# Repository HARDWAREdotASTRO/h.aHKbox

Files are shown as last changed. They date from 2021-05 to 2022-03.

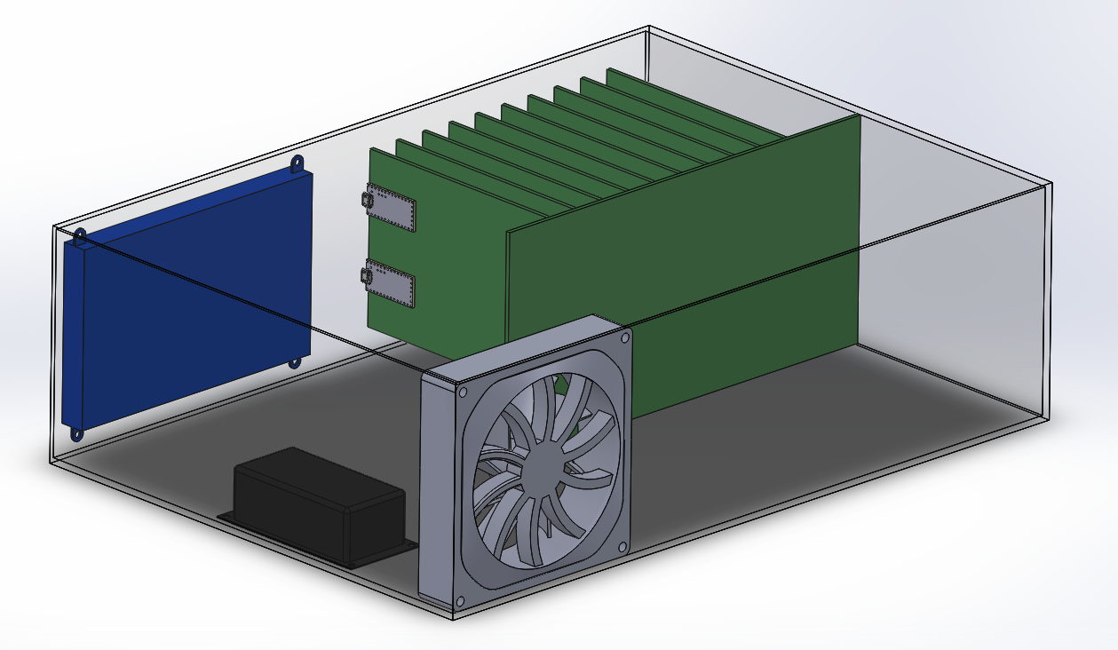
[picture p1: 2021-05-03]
Chassis/3d/Assembly - FULL/Pics/AssemblyCaptureBack0.1.PNG

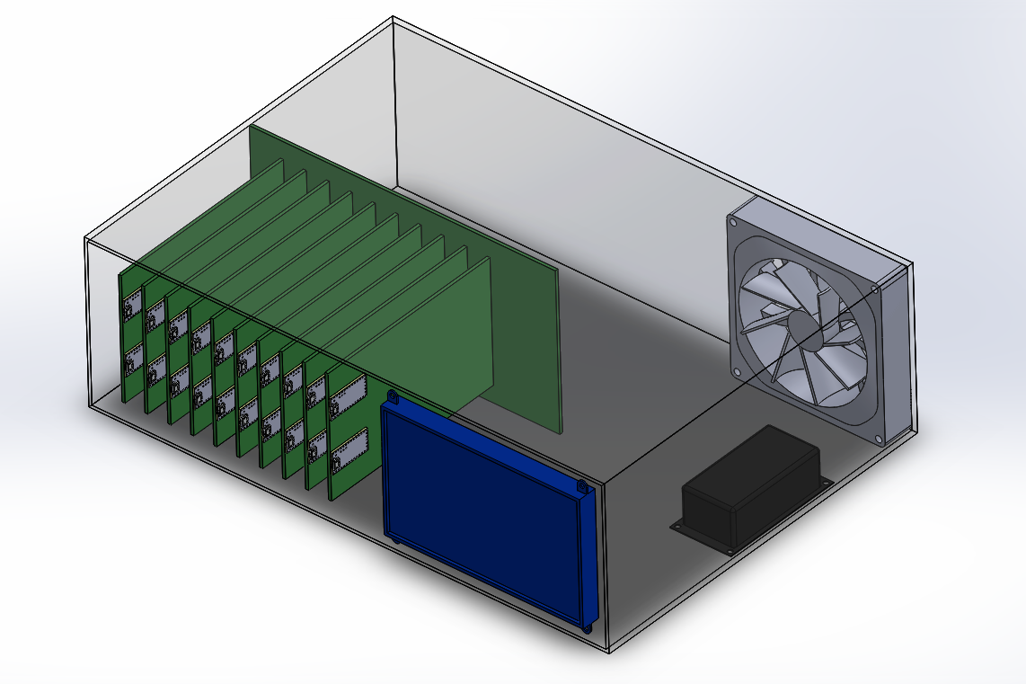
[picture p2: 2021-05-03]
Chassis/3d/Assembly - FULL/Pics/AssemblyCapture0.1.PNG

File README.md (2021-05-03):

This project was presented in progress at the 235th AAS confernece in Honolulu, HI in January of 2020. The submitted abstract for this presentation can be found here: https://ui.adsabs.harvard.edu/abs/2020AAS...23517507S/abstract

# H.aHkBox
The Hardware.astronomy Housekeeping Box (H.aHkBox) is an open source modular platform originally designed for the monitoring and control of temperatures on the ZEUS2 grating spectrometer. I began working on this project under the direction of Dr. Carl Ferkinhoff in May of 2019 and continue to do so (Dec 2020). 

Additional information about ZEUS2 can be found here: http://hosting.astro.cornell.edu/~spifiweb/zeus2/index.html

Additional information about the H.aHkBox will be made available on OSF in the future.

## Motivations
Existing temperature control equipment for the ZEUS2 is limited for various reasons. Chief among them are:
  - Obsolete components that cannot be replaced if/when they break
  - Temperature reading rate is limited by hardware multiplexer
  - System is dependent on external PC
  
The H.aHkBox is an attempt to solve these issues while providing a versatile platform for future growth of ZEUS2 and other projects.

## Specific Goals
  - [X] Design and build the chassis 
  - [X] Design and build a prototyping modular card
  - [ ] Design and build the backplane of the system [in progress]
  - [ ] Design and program an operating system (H.aHkOS) and supporting libraries [in progress]
  - [ ] Design and build ZEUS2 specific modular cards [in progress]

See h.aHKbox\Chassis\Presentation\Presentation\December 2020\ for a presentation detailing the process and current state of the project.

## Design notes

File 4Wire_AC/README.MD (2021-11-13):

<h1>4 Wire AC Expansion Card</h1>

Documentation of all firmware (in C++ for Teensy) and circuit designs for WAG implemented solution to a 4 wire AC expansion card under the H.aHK Box Project.
<br><br>

<h3>Project Background:</h3>

A 4 wire AC temperature measurement circuit is proposed for interface between the H.aHK Box (Hardware.astronomy Housekeeping Box) and the Zeus-2 Spectrometer <sup>a</sup>. Specifically, the Zeus-2 Spectrometer temperature region of interest in application of this circuit operates down to about 100 mK. The Zeus-2 spectrometer uses Lake Shore Cryogenics Interchangeable ROX sensors mainly, but also uses some Germanium GR300 sensors as well <sup>b</sup>.
<br><br>
<h3>Design Specifications</h3>
- System reports temperature value at up to 10 sps <br>
- Obtain resolution of &#177; 10mk in sub-milliKelvin scale and &#177; 1K at higher temperature ranges <br>
- Optimize (minimize) power dissipation across sensor to minimize heat dissipation into low temerature region <br>
- Optimize circuit for low component count <br>
- Digitize read in and output to circuit (frequency output, etc.) <br>
- Optically isolated sensor from digital circuitry <br>
- Operature through +5V and +24V lines <br>
- Interface with H.aHK Box systems and software/firmware communication protocols <br>
<br><br>

<h3>Project Staff</h3>
- Stephen Shaw (General Engineering, Electronics), May 2020 - May 2022

<br><br>
<h3>References</h3>
<sup>a</sup> - https://www.researchgate.net/publication/47351146_ZEUS-2_A_second_generation_submillimeter_grating_spectrometer_for_exploring_distant_galaxies
<br>
<sup>b</sup> - https://www.lakeshore.com/products/categories/temperature-products/cryogenic-temperature-sensors

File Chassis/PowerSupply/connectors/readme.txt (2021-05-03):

Power connector information in this folder

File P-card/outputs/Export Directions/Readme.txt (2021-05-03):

I had a lot of trouble with exporting from CircuitMaker, but eventually I figured it out!

I strongly recommend you use the "Outputs" tab while editing a circuitboard file, rather than "Project -> Generate Outputs" as the latter option generates all outputs for every board in the project which can get confusing.

Issues I ran into:
1. "Board Cutout" and "Board Shape" have nothing to do with the actual board shape. They are just there so you know where you can put your components. To tell the manufacturer the shape of the board you need to use lines to draw the board outline on the "Keep-out Layer" Layer. 
	-> If there is no pre-existing keepout layer, you can open the "View Configurations" Layer window by clicking on the small colored rectangle to the left of the layer tabs at the bottom of the circuit board window. This should list all of the layers and their colors. From here you want to look at the Mechanical Layers(M) table on the top right. Uncheck the "Only show enabled mechanical Layers" box if it is checked. Enable one of the unused Mechanical Layers using the "Enable" check box. Slowly click twice on the name of the layer so you're able to edit the name. Rename it to "Outline". Check the "Show" box for this layer, and then click "OK" at the bottom right of the window. Now you should have the "Outline" Layer listed in the tabs at the bottom, and you can draw your board outline.

2. Wonky Top Overlay drawings resulted in the Gerber Viewer when I uploaded the files wihtout any explanation. I had followed the same process that worked not 20 minutes prior to export my files, so I had no idea what caused it. After a lot of creative googling I found one forumn post where someone suggested use "Relative Origin" instead of "Absolute Origin" in the file output configurations. This did indeed fix my issue, but you NEED to make sure you use relative origin for both the gerber output and the nc drill output. If they arn't the same, the holes may end up offset!

OUTPUT STEPS:
1. Save your files and commit them.
2. With your board file open, goto the "Outputs" tab and click the "Gerber" button.
		- if you are prompted to save, click yes, click ok
3. In the pop up you can change your setting as needed. The mains ones I messed with:
		General -> Units = millimeters
		General -> Format = 4:3
		Layers -> All Layers -> Plot = checked (everything else unchecked
					-----> if you used a mechanical layer instead of the "Keep-out layer", make sure its "Plot" checkbox is checked in the right side of this layer tab. Otherwise it won't be part of the outputs.
		Drill Drawings -> Plot all used layer pairs = both boxes checked
		Apertures -> Embedded apertures (RS274X) = checked
		Advanced -> Position on File = Reference to relative origin
		Everything else left default
4. Click OK and save to desired location

5. In the Outputs tab, click "NC Drill Files" and save/commit if prompted.
6. Settings I chose are as follows
		Units = Millimeters (same as gerber)
		Format = 4:3 (same as gerber)
		Coordinate Positions = Reference to relative origin (same as gerber)
		Everything else left default
7. Click OK and save to desired location (preferably near gerber output)
8. Next, the gerber and NC Drill files need to be combined into one zip file. 
	- Using your desired program, Extract the contents of both the gerber output and the nc drill output.
	- Create a new zip file and add both outputs to it.
		- You will be prompted to overwrite the StatusReport.txt, to which you can say yes.
9. The resulting zip is the file you will need to upload to the manufacturer.
10. I suggest you use an online Gerber Viewer to make sure the files load in the way you expect them to. 
		https://www.pcbway.com/project/OnlineGerberViewer.html   is what I used as we were ording from PCBWay anyway. If you're ordering from a different manufacturer and they have a their own viewer, I suggest you use theirs as it will likely be more accurate to their process.

If you have any questions you can contact me at adam.stammer@go.winona.edu or adam.r.stammer@gmail.com

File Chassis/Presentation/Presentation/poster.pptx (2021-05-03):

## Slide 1

HARDWARE.astronomy: Housekeeping Box (H.aHkBox)

Here we present the HARDWARE.astronomy Housekeeping Box (H.aHkBox). The H.aHkBox is a low-cost open-source temperature monitoring and control system. It employs existing open-source devices (e.g Arduino, RaspberryPi) to reduce costs while also limiting the complexity of the development. The H.aHkBox features a chassis with a variety of capabilities, a control computer, and 10 expansion slots that can be populated by expansion cards. The first deployment of the H.aHkBox will be for the ZEUS-2 submillimeter grating spectrometer. As such the modular cards will include AC and DC excited 4-wire bridges, 2-wire bridge, and PID controller card. The system can output up to 200W, and achieve sub-millikelvin temperature sensing accuracy. Design, firmware, software and parts list will be published online allowing for other projects to adopt the system and create custom expansion cards as needed. Here we provide an overview of the project, initial layout of the chassis, electrical design, and specifications, as well as a proto-type expansion card.

Abstract

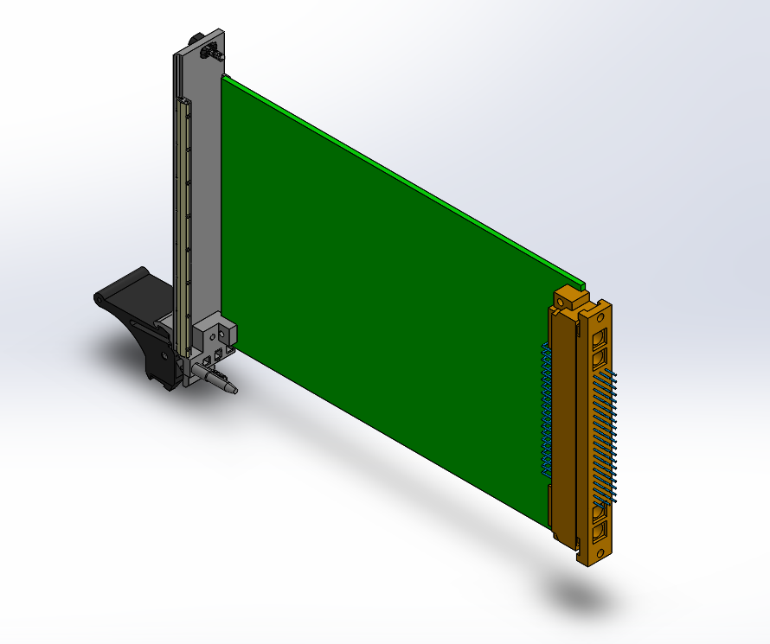
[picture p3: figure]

Background/Requirements

Prototyping Card

Backplane

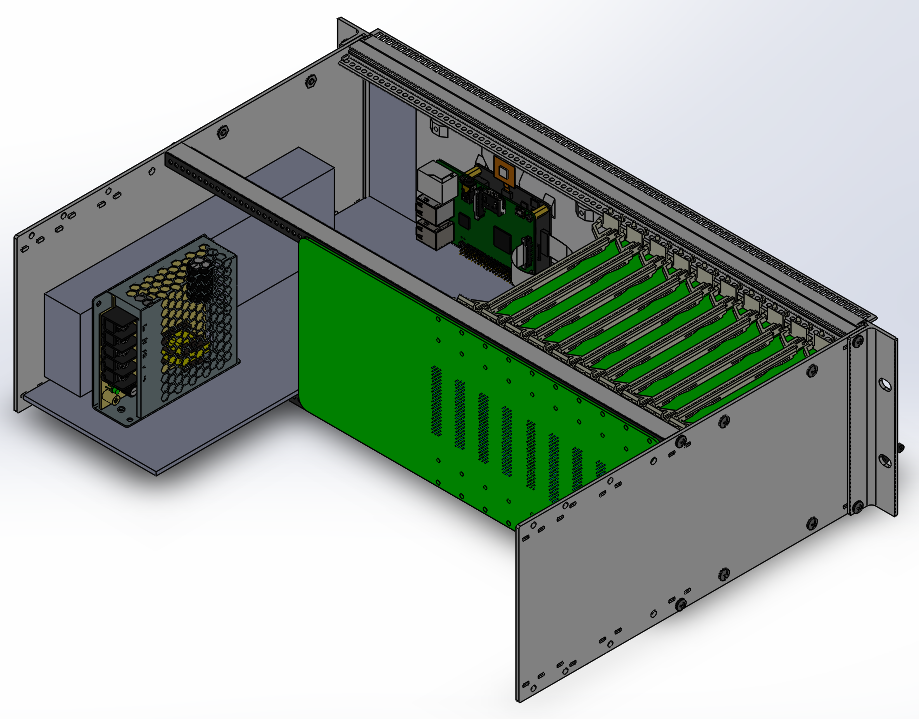
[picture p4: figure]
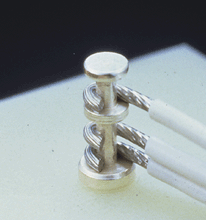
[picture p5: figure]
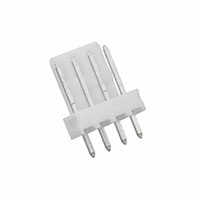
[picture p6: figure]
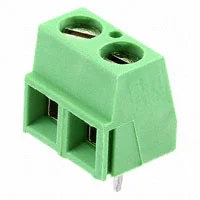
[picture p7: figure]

Interface

Physical Design and Interface

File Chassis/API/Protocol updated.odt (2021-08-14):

Logistical Header | Source Card Type | [Data Frame 1] | [Data Frame 2] | [Data …] | [Data Frame n]

0 4 8 16 24 32 n

Logistical Header:

Logistical Request → (0x0) Used to poll Followers for information.

Logistical Response → (0x1) Responds to Logistical Request. Followed by yes/no data frame.

Error → (0x2) Used to report an error.

Data → (0x3) Used to send non-logistical data.

Acknowledgement (0x4) Sent to follower devices to say message was received

Boot (0x5) When booting up sends information to slave

Interrupt (0x6) Allows for slaves to interrupt connection

Command Request (0x7) request to send a command to Follower device

Command Response (0x8) Responds to receive message of command (acknowledges before performing the command

Logistical Request Format

0b0000 | Source Card Type

0 4 8

This is sent to a slave to ask if there is any message for the master to read from it. The slave will always respond with a logistical response. If the Logistical Request times out, it will be viewed as an error. In such a timeout case, the slave may be assumed non-responsive or not installed into the motherboard and may be taken out of the communication update loop.

Logistical Response Format

0b0001 | Source Card Type | (0b0 / 0b1) , Buffer Size

0 4 8 9 16

This is sent back to the master in response to a Logistical Request. It contains only the Logistical Header and one 8-bit data frame. The first bit in the data frame answers a yes or no to the question. 0 indicates that there is data to read from the slave, while a 1 indicates that there is not. The remaining 7 bits in this data frame denote the amount of sequential bits of data to be read. Since I2C reads 8-bit data frames, rather than direct bits, it is suggested that any data is built in 8 bit blocks, though extra bits can simply be ignored.

Error

0b0010 | Source Card Type | Error Type

0 4 8 16

The Error Header is used to report an error to the master. Error Type is an 8-bit data frame that denotes the error code. These error codes will be card specific, so they can only be defined as part of the card design. Since there are 16 reportable card types and one 8-bit data frame for the error code, it’s suggested that error codes are defined by card type as denoted below, though this isn’t required.

Card Type | Error Code Range | Card Type | Error Code Range
0 | 0-4095 | 8 | 32768-36863
1 | 4096-8191 | 9 | 36864-40959
2 | 8192-12287 | A | 40960-45055
3 | 12288-16383 | B | 45056-49151
4 | 16384-20479 | C | 49152-53247
5 | 20480-24575 | D | 53248-57343
6 | 24576-28671 | E | 57344-61439
7 | 28672-32767 | F | 61440-65535

Data

4-wire AC (Card Type 0x2)

Input

0b0011 | 4 wire AC (card) | Specific Card Data ---- >

0 4 8 48

4 - Wire AC (Card Data)

Channel number | On/Off | Voltage flag | Range | 32-bit Resistance data
0b000 | 0b0 | 0b0 | 0b000 | 0b0000 0000 0000 0000…. 0000
0b001
0b010
0b011

8 11 12 13 16 48

Channel number:

4 channels each on will contain a setting for whether the channel will be on or off and what the range that channel will be.

On/Off:

1 value for on

0 Value for off

Voltage flag:

Using the extra byte from the range to be a voltage flag. When 1 it means the number is returning a voltage when low it is returning a resistance value

Range:

| Range

0 4

Represent the possible range of resistance that can be used by the 4 wire ac. This uses only three bits originally it was 4 with a buffer zero value but the extra zero bit is now going to be used a Boolean to represent if the data being received is a voltage or a resistance.

Flag | 000 | 10K Ω
| 001 | 100KΩ
| 010 | 1MΩ
| 011 | 10MΩ

0 1 4

16 bit Resistance Data

If we are using decimal numbers in returning back resistance values then the

*Changed to 32 bits precision of byte data*

This is intended to be a scientific notation of data

8 bits to represent the whole number with 24 bits of decimal point precision using mantissa binary numbers

Some bits will be reserved to represent as an exponential value.

Currently we can used the last 8 bits of the 24 decimal point precision as exponential (max value of 255) or signed bit ( 127 to -128)

Higher resistance is needed for when it gets below 1 K due to self heating

Difference modes when different resistors are attached to the 4 wire ac card

The card will have to convert the voltage or resistance into scientific notation. The scientific notation of the conversion will be displayed onto the GUI.

4 Channels

Measuring 4 temperatures (change in resistance) uses 16 bits of double precision

Returns a resistance that ranges from ~100ohm to 100Kohm

Error:

Time out

Could not detect master – time out

Could not understand master request

Value in sent to device does not make sense

Boot

0b0100 | Source card

0 4 8

The initial message the master sends out for slaves to respond to. The slaves are to respond with their typical logistical response with what card they are but they will have no data attached to them, so they will send all zeros. On this initial boot the Master will wait for a response from each possible card and then add each card to the round Robin while loop if the corresponding source card responds within a certain time limit. There is a possible of 10 max cards so the increment of the source card number will max at 10 (Actually at 0b0111)

Interrupt

0b0101 | Source Card Type | Interrupt data

0 4 8 16

Triggers an interrupt to happen to allow the card to break the master out of the Round Robin. It has the interrupt trigger and what source card and telling the master what it wants to do. The master will handle the Interrupt before going back to what it was doing. Once the interrupt is finished the master will continue its while loop rounds of all the cards registered as slaves, checking for information.

Command Request

0b0111 | Source card type | Command type list

This will be used by the Leader device to send to Follower to have them perform a command

Possible commands to be used (functions vary from card to card):

Shutdown

Change settings

Temp

Voltage or resistance data

Resistance range

Command Response

0b1000 | Source card type | Data?

0 4 8

An acknowledgement that the card has received the command.

(card will acknowledge After doing command)

Not sure if a data portion is going to be needed could be used as something similar to logistical requestion to write if the card has any new data to report after the command has been executed. (NOTE: if data portion is not needed then the acknowledgement can be send before performing the command. This data can also instead be sent as either a regular round robin or a interrupt instead)

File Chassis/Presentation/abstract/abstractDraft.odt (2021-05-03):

Abstract (H.aHKbox)

Here we present the HARDWARE.astronomy Housekeeping Box (H.aHKbox. The H.aHKbox is a low-cost open-source temperature monitoring and control system, which employs existing open-source devices (e.g Arduino, RaspberryPi) to reduce costs while also limiting the complexity of the development. The Ha.HK Box features a base system with a control computer and 10 expansion slots that can be filled with a variety of expansion cards.

The first deployment of the Ha.Hkbox will be for the ZEUS-2 submillimeter grating spectrometer. As such the modular cards will include AC and DC excited 4-wire bridges, 2-wire bridge, and PID controller card. The system will achieve power outputs of up to 200W with sub-millikelvin temperature sensing accuracy.

All design, firmware, software and parts list will be published online allowing for other projects to adopt the system and create custom expansion cards as needed.

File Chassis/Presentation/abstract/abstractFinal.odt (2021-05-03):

HARDWARE.astronomy: Housekeeping Box (H.aHk Box)

Here we present the HARDWARE.astronomy Housekeeping Box (H.aHk Box). The H.aHk Box is a low-cost open-source temperature monitoring and control system. It employs existing open-source devices (e.g Arduino, RaspberryPi) to reduce costs while also limiting the complexity of the development. The H.aHk Box features a chassis with a control computer, and 10 expansion card slots that can achieve a variety of capabilities. The first deployment of the H.aHk Box will be for the ZEUS-2 submillimeter grating spectrometer. As such the modular cards will include AC and DC excited 4-wire bridges, 2-wire bridge, and PID controller card. The system can output up to 200 watts, and achieve sub-millikelvin temperature sensing accuracy. The schematics, firmware, software and parts list will be published online allowing for other projects to adopt the system and create custom expansion cards as needed. Here we provide an overview of the project, initial layout of the chassis, electrical design, and specifications, as well as a proto-type expansion card.

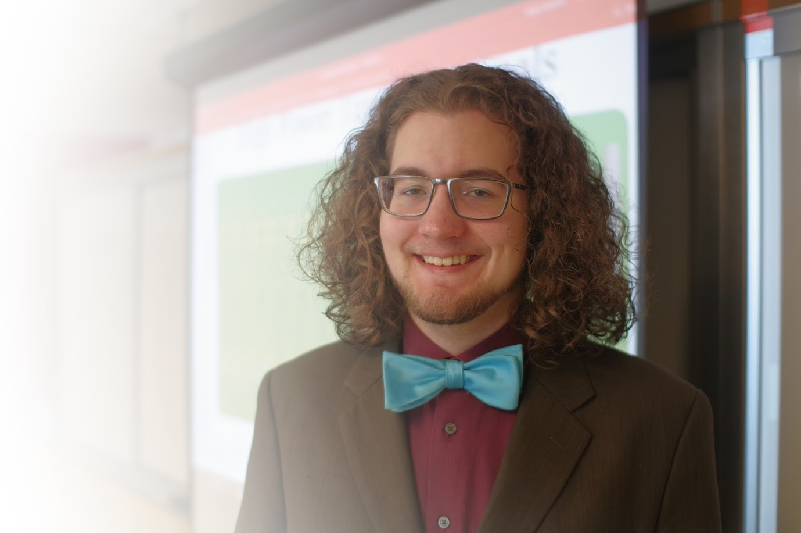
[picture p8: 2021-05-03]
Chassis/Presentation/Presentation/figures/posterPhoto.png

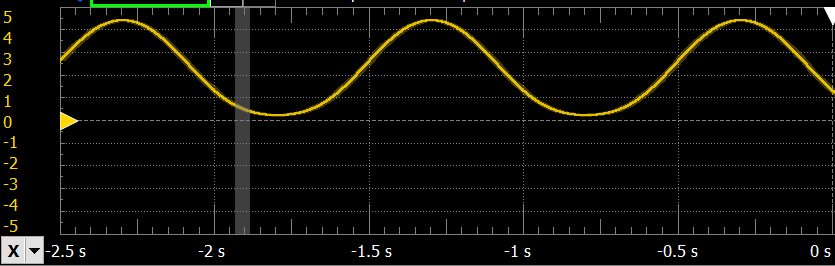
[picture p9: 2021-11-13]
4Wire_AC/LabFiles/LAB004_DesignViabilityAnalysis/Part1_Trace_Vmod1.PNG

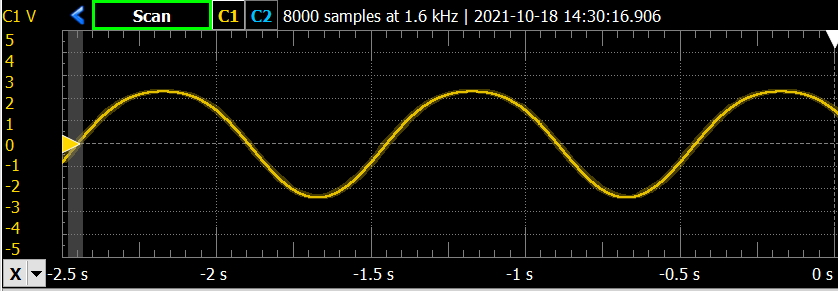
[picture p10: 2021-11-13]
4Wire_AC/LabFiles/LAB004_DesignViabilityAnalysis/Part1_Trace_InstAmp.PNG

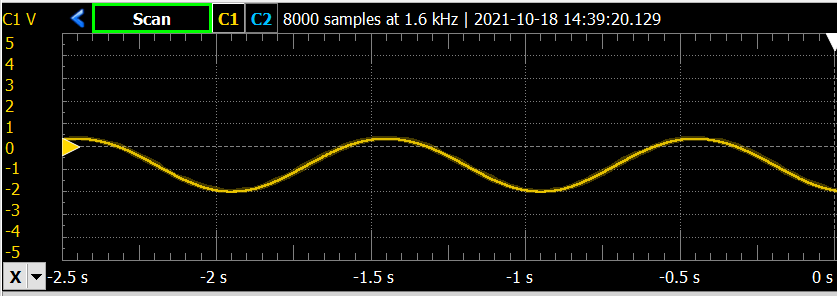
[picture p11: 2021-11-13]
4Wire_AC/LabFiles/LAB004_DesignViabilityAnalysis/Part1_Trace_InstAmp2.PNG

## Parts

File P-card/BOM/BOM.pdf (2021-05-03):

Sheet1

All Prices Are Subject to Change | Compiled July of 2019 by Adam Stammer
All Prices Based On Single Unit Price

P-Card BOM
Part Name/Description | Supplier Part # | Supplier | Manufacturer Mfct. Part # Unit Cost | Quantity | Total Cost
P-Card PCB | Varies | 1 Varies
Female Socket | 1195-4236-ND | Digikey | Harting | 9032606865 | 9.48 | 1 | 9.48
Male Socket | 1195-1147-ND | Digikey | Harting | 9031606901 | 10.67 | 1 | 10.67
Banana Jack | BKCT3151SP-0-ND | Digikey | Cal Test Electr CT3151SP-0 | 2.05 | 4 | 8.2
Breadboard (10”x3.5” max) | BKGS-830-ND | Digikey | Global Special | GS-830 | 8.25 | 1 | 8.25
Teensy 3.x | 1528-2385-ND | Digikey | Adafruit Indust | 2756 | 24.94 | 1 | 24.94
RA Din-Signal Hi Current Pin | 1195-1112-ND | Digikey | Harting | 9030006104 | 7.22 | 2 | 14.44
Total (USD) | 75.98

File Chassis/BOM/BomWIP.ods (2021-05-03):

All Prices Are Subject to Change | Compiled July of 2019 by Adam Stammer
All Prices Based On Single Unit Price
P-Card BOM
Part Name/Description | Supplier Part # | Supplier | Manufacturer | Mfct. Part # | Unit Cost | Quantity | Total Cost
P-Card PCB |  |  |  |  | Varies | 1 | Varies
Female Socket | 1195-4236-ND | Digikey | Harting | 9032606865 | 9.48 | 1 | 9.48
Male Socket | 1195-1147-ND | Digikey | Harting | 9031606901 | 10.67 | 1 | 10.67
Banana Jack | BKCT3151SP-0-ND | Digikey | Cal Test Electronics | CT3151SP-0 | 2.05 | 4 | 8.2
Breadboard (10”x3.5” max) | BKGS-830-ND | Digikey | Global Specialties | GS-830 | 8.25 | 1 | 8.25
Teensy 3.x | 1528-2385-ND | Digikey | Adafruit Industries | 2756 | 24.94 | 1 | 24.94
RA Din-Signal Hi Current Pin | 1195-1112-ND | Digikey | Harting | 9030006104 | 7.22 | 2 | 14.44
 |  |  |  |  |  | Total (USD) | 75.98
Backplane BOM
Part Name/Description | Supplier Part # | Supplier | Manufacturer | Mfct. Part # | Unit Cost | Quantity | Total Cost
Backplane PCB |  |  |  |  | Varies | 1 | Varies
Female Socket | 1195-4236-ND | Digikey | Harting | 9032606865 | 9.48 | 10 | 94.8
4 Pin Socket | WM50016-04-ND | Digikey | Molex | 22284043 | 0.4 | 90 | 36
2 Pos Screw Terminal | 283-4439-ND | Digikey | Eaton – Electctronics Div. | EM250502V | 1.01 | 12 | 12.12
Turret Terminal | 952-1453-ND | Digikey | Harwin Inc. | H9021-01 | 0.43 | 33 | 14.19
 | Z9021-00-ND | Digikey | Harwin Inc. | Z9021-00 | 343.68 | 1 | 343.68
Arduino Uno Rev 3 | Rev 3 | Arduino Store | Arduino | Rev 3 | 22 | 1 | 22
Arduino Heads | 1528-1074-ND | Digikey | Adafruit Industries | 85 | 1.95 | 1 | 1.95
7 Segment LED Single Digit Display | 516-1213-5-ND | Digikey | Broadcom Limited | HDSP-5503 | 2.77 | 1 | 2.77
Raspberry PI GPIO Header Pins | 1568-1675-ND | Digikey | SparkFun Electronics | PRT-14275 | 0.95 | 1 | 0.95
Raspberry Pi GPIO Socket | 1528-1947-ND | Digikey | Adafruit Industries | 1658 | 1.75 | 1 | 1.75
LED 5mm Round TH | C503B-RAN-CZ0C0AA2CT-ND | Digikey | Cree Inc. | C503B-RAN-CZ0C0AA2 | 0.15 | 2 | 0.3
150-300 Ohm Resistor | CF14JT330RCT-ND | Digikey | Stackpole Electronics | CF14JT330R | 0.1 | 15 | 1.5
Shift Register | 296-8251-5-ND | Digikey | Texas Instruments | SN74HC165N | 0.48 | 2 | 0.96
16 Pos DIP Socket | AE9992-ND | Digikey | Assmann WSW Components | A 16-LC-TT | 0.25 | 1 | 0.25
S Din-Signal Hi Current Pin | 1195-1123-ND | Digikey | Harting | 9030006225 | 13.75 | 20 | 275
 |  |  |  |  |  | Total | 808.22
Chassis/Other BOM
Part Name/Description | Supplier Part # | Supplier | Manufacturer | Mfct. Part # | Unit Cost | Quantity | Total Cost
Case | CCA27-84-01-ND | Digikey | Vector Electronics | CCA27-84-01 | 195.64 | 1 | 195.64
Front Panel | V2029-ND | Digikey | Vector Electronics | FP52B4HP-1 | 11.36 | 10 | 113.6
Card Guide | V2008-ND | Digikey | Vector Electronics | 3250-0001-01 | 2.9 | 10 | 29
Ejector | V2063-ND | Digikey | Vector Electronics | 90100002-1 | 19.11 | 10 | 191.1
Raspberry Pi GPIO Ribbon Cable | 1528-2235-ND | Digikey | Adafruit Industries | 1988 | 2.95 | 1 | 2.95
Raspberry Pi Model 3 B+ | 1690-1025-ND | Digikey | Raspberry Pi foundation | RASPBERRY PI 3 MODEL B+ | 41.56 | 1 | 41.56
24V Power Supply | 1866-4968-ND | Digikey | Mean Well USA Inc. | UHP-350-24 | 77.33 | 1 | 77.33
5V Power Supply | 1866-3329-ND | Digikey | Mean Well USA Inc. | LRS-150F-5 | 27.84 | 1 | 27.84
7” Touch Screen | 1528-1813-ND | Digikey | Adafruit Industries LLC | 2407 | 89.95 | 1 | 89.95
Temp Sensor (Analog) | TMP36GT9Z-ND | Digikey | Analog Devices Inc. | TMP36GT9Z | 1.49 | 3 | 4.47
8 Pos DIP Socket | AE9986-ND | Digikey | Assmann WSW Components | A 08-LC-TT | 0.18 | 3 | 0.54
AC Power Cable | Q102-ND | Digikey | Qualtek | 312007-01 | 5.35 | 1 | 5.35
AC Power Socket | Q336-ND | Digikey | Qualtek | 703W-00/08 | 0.88 | 1 | 0.88
 |  |  |  |  |  | Total | 244.64
 |  |  |  |  | Total Price of this BOM |  | 1128.84

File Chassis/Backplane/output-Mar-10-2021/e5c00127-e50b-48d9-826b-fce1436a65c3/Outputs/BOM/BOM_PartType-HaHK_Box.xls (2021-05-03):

Comment | Description | Designator | Footprint | LibRef | Quantity
Arduino Uno | Microcontroller board, Uno [Arduino] A000066 Microcontroller board, Uno 7640152110092 | AUNO | PCB-5e3n8s0ey5jqr2f9nncc-1 | CMP-1073962-71 | 1.0
Molex 22-28-4043 | Conn; Rect./PCB; Breakaway Header; 4 Cir.; Vert.; KK 254 Ser.; Gold Plate; 6.09mm Pin L | CH1, CH-A1, CH-A2, CH-A3, CH-A4, CH-A5, CH-A6, CH-A7, CH-A8, CH-A9, CH-B1, CH-B2, CH-B3, CH-B4, CH-B5, CH-B6, CH-B7, CH-B8, CH-B9, CH-C1, CH-C2, CH-C3, CH-C4, CH-C5, CH-C6, CH-C7, CH-C8, CH-C9, CH-D1, CH-D2, CH-D3, CH-D4, CH-D5, CH-D6, CH-D7, CH-D8, CH-D9, CH-E1, CH-E2, CH-E3, CH-E4, CH-E5, CH-E6, CH-E7, CH-E8, CH-E9, CH-F1, CH-F2, CH-F3, CH-F4, CH-F5, CH-F6, CH-F7, CH-F8, CH-F9, CH-G1, CH-G2, CH-G3, CH-G4, CH-G5, CH-G6, CH-G7, CH-G8, CH-G9, CH-H1, CH-H2, CH-H3, CH-H4, CH-H5, CH-H6, CH-H7, CH-H8, CH-H9, CH-I1, CH-I2, CH-I3, CH-I4, CH-I5, CH-I6, CH-I7, CH-I8, CH-I9, CH-J1, CH-J2, CH-J3, CH-J4, CH-J5, CH-J6, CH-J7, CH-J8, CH-J9 | HEADER_1x4 | CMP-44448d4a5f9d9b83-3 | 91.0
Maxim Integrated DS18B20+ | DS18B20+ /Maxim Integrated (Dallas)/ Digital temperature sensor, TO-92, -55/+125C, RoHS | DTMP-A, DTMP-B, DTMP-C | PCB-6xl7qimvuxkxf3clfff9-1 | CMP-3808910-8 | 3.0
4.7kOhm | Res Metal Film 4.7K Ohm 1% 3/5W ±50ppm/°C Conformal AXL Thru-Hole Ammo Pack | DTMP-RES, PUR-SCL2, PUR-SDA1, PUR-SDA2, PUR-SLC1 | PCB-3trqkg5dul8e4bq69e8d-1 | CMP-2511ecee5430fad6-2 | 5.0
SYM-dgd04bf3j3drhl5uyyz7-1 | CONN DIN RCPT 64POS PCB GOLD | FE, S-A, S-B, S-C, S-D, S-E, S-F, S-G, S-H, S-I, S-J | PCBComponent_1 - duplicate | CMP-dgd04bf3j3drhl5uyyz7-22, CMP-dgd04bf3j3drhl5uyyz7-27, CMP-dgd04bf3j3drhl5uyyz7-27, CMP-dgd04bf3j3drhl5uyyz7-27, CMP-dgd04bf3j3drhl5uyyz7-27, CMP-dgd04bf3j3drhl5uyyz7-27, CMP-dgd04bf3j3drhl5uyyz7-27, CMP-dgd04bf3j3drhl5uyyz7-27, CMP-dgd04bf3j3drhl5uyyz7-27, CMP-dgd04bf3j3drhl5uyyz7-27, CMP-dgd04bf3j3drhl5uyyz7-27 | 11.0
EM250502V | Conn Terminal Block 2 POS 5.08mm Screw ST Cable Mount 16A | GND, HPO-A, HPO-B, HPO-C, HPO-D, HPO-E, HPO-F, HPO-G, HPO-H, HPO-I, HPO-J, P_IN | PCB-u2v43o1ftwqs3duy389i-1 | CMP-9ab5517917744572-4, CMP-9ab5517917744572-6, CMP-9ab5517917744572-6, CMP-9ab5517917744572-6, CMP-9ab5517917744572-6, CMP-9ab5517917744572-6, CMP-9ab5517917744572-6, CMP-9ab5517917744572-6, CMP-9ab5517917744572-6, CMP-9ab5517917744572-6, CMP-9ab5517917744572-6, CMP-9ab5517917744572-4 | 12.0
1502-2 | Brass Bright Tin Plate .219 inch High for .109 inch Board Width Turret Terminal | GND-A, GND-B, GND-C, GND-D, GND-E, GND-F, GND-G, GND-H, GND-I, GND-J, HP-A, HP-B, HP-C, HP-D, HP-E, HP-F, HP-G, HP-H, HP-I, HP-J, LP-A, LP-B, LP-C, LP-D, LP-E, LP-F, LP-G, LP-H, LP-I, LP-J | PCB-3pxxqie2fct8emy2m3uy-1 | CMP-0157c85d593dde90-2 | 30.0
Keystone 1502-2 | Brass Bright Tin Plate .219 inch High for .109 inch Board Width Turret Terminal | GND-MAIN, HP-MAIN, LP-MAIN | PCB-3pxxqie2fct8emy2m3uy-1 | CMP-0157c85d593dde90-2 | 3.0
61300211121 | THT Vertical Pin Header WR-PHD, Pitch 2.54 mm, Single Row, 2 pins | GND1, GND2, PWR1, PWR2 | PCB-omgsbkhp90n7lpri88og-1 | CMP-748fbcb73d6bab48-27 | 4.0
Cal Test Electronics CT3151SP-0 | 4MM Safety Jack , Horizontal Pcb Mount Black | HPIA, HPIB, HPOA, HPOB, PWR-5V | PCB-y1ci8m7vwvotsse2jq9i-1 | CMP-869a4c9259de595d-9 | 5.0
Würth Elektronik 61300621121 | THT Vertical Pin Header WR-PHD, Pitch 2.54 mm, Dual Row, 6 pins | I2C1, I2C2 | PCB-zvoyfznuc9b5lzhitk0z-1 | CMP-8aac4253fa23556b-5 | 2.0
09031606901 | Conn DIN 41612 M 60Power/4Coaxial POS 2.54mm Solder RA Thru-Hole | MA | PCB-uzhe8vs3bcqz6bzs18qy-1 | CMP-dd70146577e902b7-11 | 1.0
Raspberry Pi 2+/3 | Dev Brd, Rpi Model b, Bcm2835 Processor | RPI | Header Only | CMP-e7ab2d993b99386c-20 | 1.0
TMP36GT9 | Low Voltage Temperature Sensor, 2.7 to 5.5 V Supply, Industrial, 3-pin TO92 (T-3), Tray | TMP36-1, TMP36-2, TMP36-3 | ADI-T-3 | CMP-2418272-2 | 3.0

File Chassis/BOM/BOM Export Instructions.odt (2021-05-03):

How I export the Bill of Material from LibreOffice Calc as a PDF file:

In the top menu bar click “Format”.

From the dropdown select “Page”.

In the popup select the “Page” tab.

*Fill in the values as described below:

Width: 12.00”

Height: 8.50”

Orientation: Landscape

All Margins: 0.50”

Click the OK button at the bottom of the popup to confirm your settings.

In the top menu bar click “File”.

From the dropdown select “Export as PDF...”

A save prompt should appear which will allow you to choose a save location.

*This formatting is subject to change and is not a standardized format. You’re welcome to use this as a starting point and change things as you feel inclined.

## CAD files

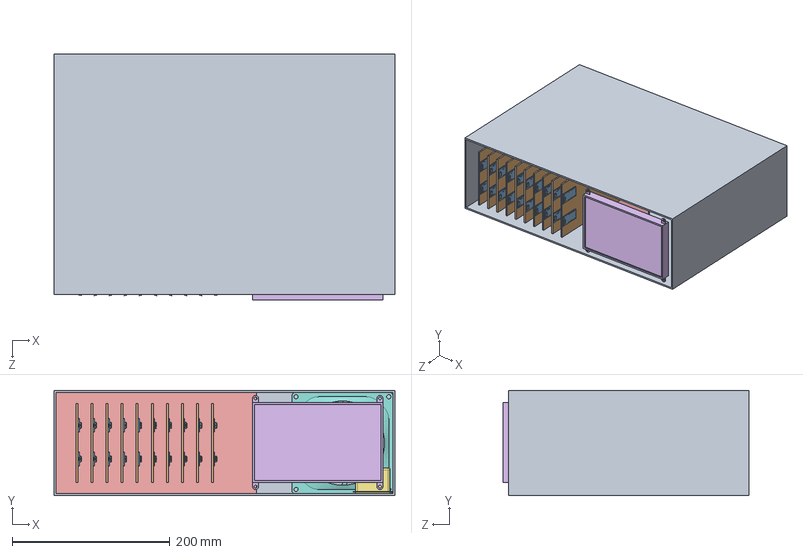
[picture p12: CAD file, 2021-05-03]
Chassis/3d/Assembly - FULL/FullAssembly.SLDASM
431.8 x 133.4 x 312.1 mm
RackCasing
Eurocard x 10
Teensy 3.1 PCB x 20
micro_usb_47346-0001 x 20
Backplane
Display
PowerSupply
Fan

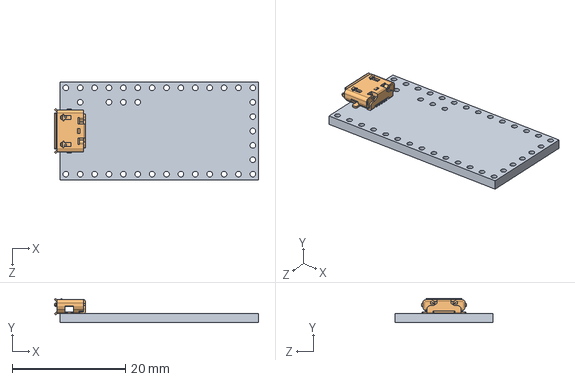
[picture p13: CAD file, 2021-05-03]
Chassis/3d/Assembly - FULL/Teensy/Teensy 3.1.SLDASM
36.0 x 4.30 x 17.2 mm
Teensy 3.1 PCB
micro_usb_47346-0001

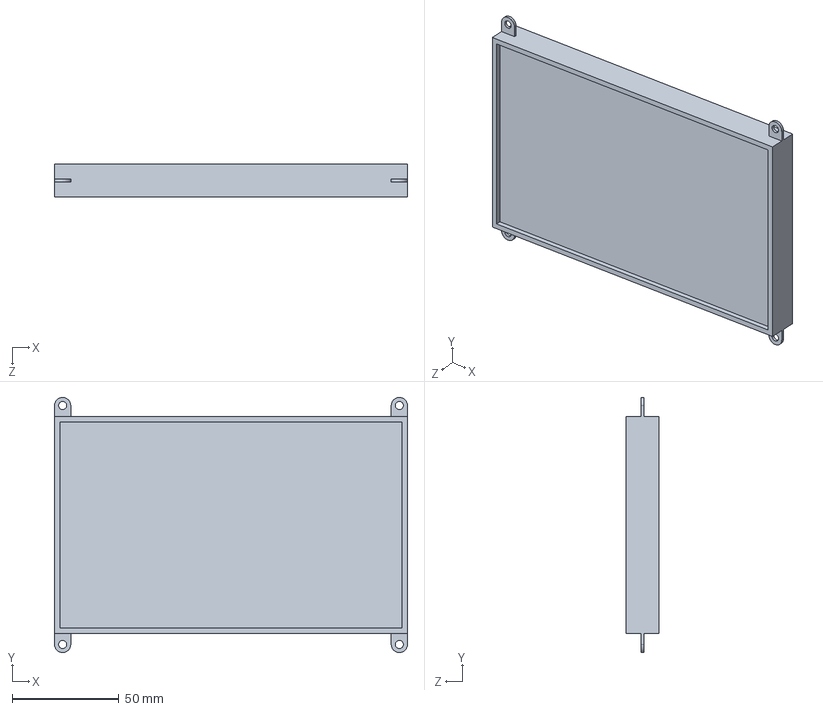
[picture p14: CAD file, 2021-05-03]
Chassis/3d/Assembly - FULL/Display.SLDPRT
165.1 x 119.4 x 15.2 mm

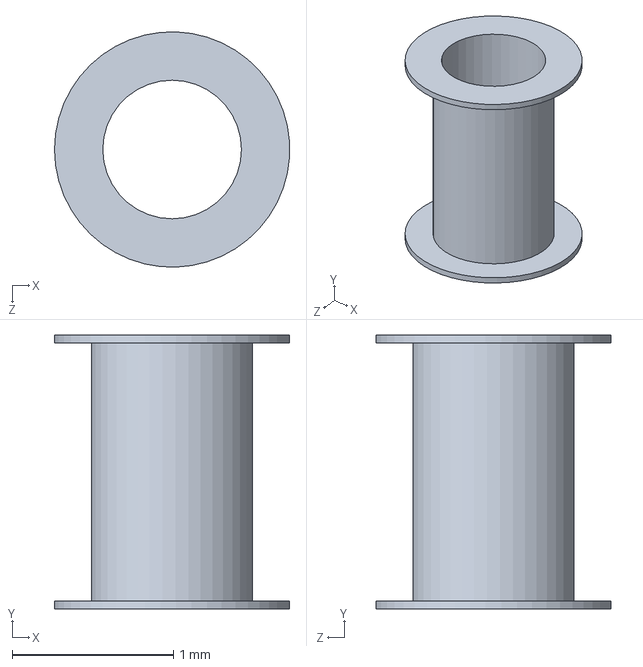
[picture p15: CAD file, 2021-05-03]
Chassis/3d/Assembly - FULL/Teensy/Hole metalization.SLDPRT
1.46 x 1.70 x 1.46 mm

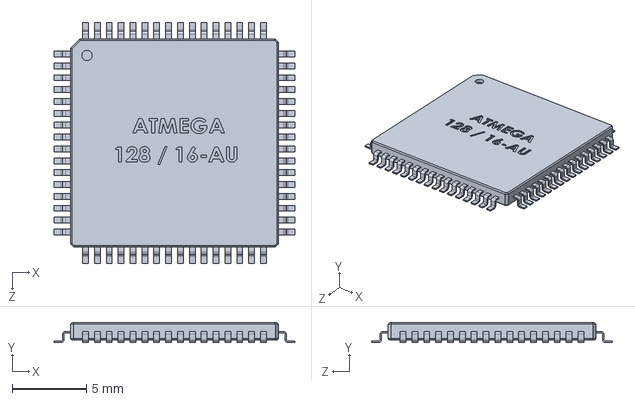
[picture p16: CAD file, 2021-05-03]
Chassis/3d/CaseAssembly/TQFP64.SLDPRT
16.2 x 1.36 x 16.2 mm

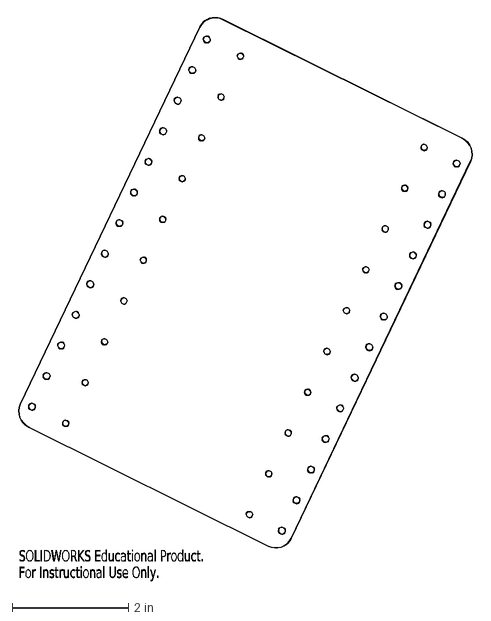
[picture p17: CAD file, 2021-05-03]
Chassis/Backplane/BackPlane #1.DXF
SOLIDWORKS Educational Product.
For Instructional Use Only.

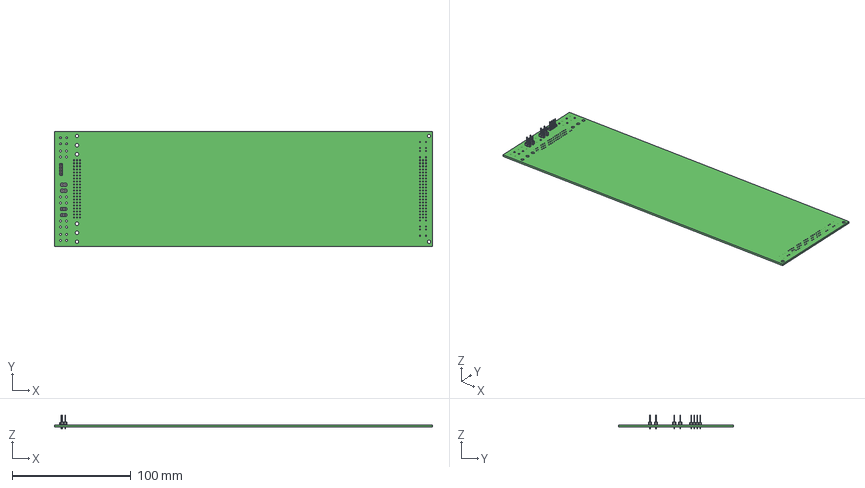
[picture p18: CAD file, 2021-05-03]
Chassis/Backplane/output-Mar-10-2021/e5c00127-e50b-48d9-826b-fce1436a65c3/Outputs/ExportSTEP/PCardWBJ.step
318.0 x 96.6 x 11.8 mm
BoardPCardWBJ
User_Library-HDR1X1_Rectangular_Straight x 8
Molex_22-28-4xx3_v1 x 4

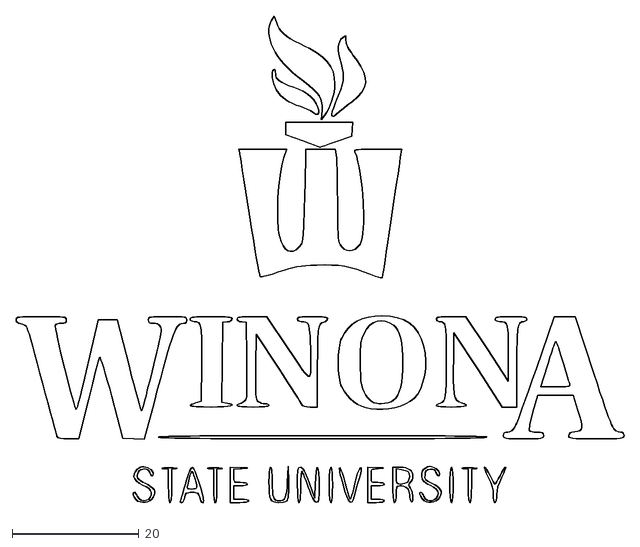
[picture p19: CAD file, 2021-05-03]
Chassis/Presentation/WSU_Logo_digital_use/wLogoFlameTop.dxf
96.0 x 77.5

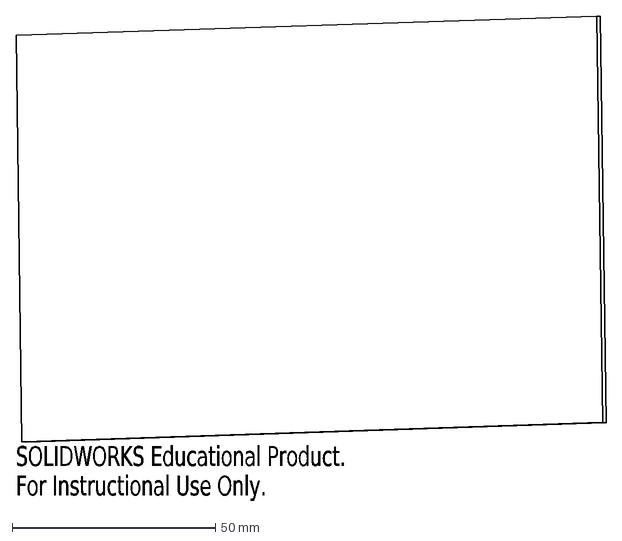
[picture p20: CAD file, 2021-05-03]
P-card/potentially-useful-3d/Expansion Card.DXF
SOLIDWORKS Educational Product.
For Instructional Use Only.

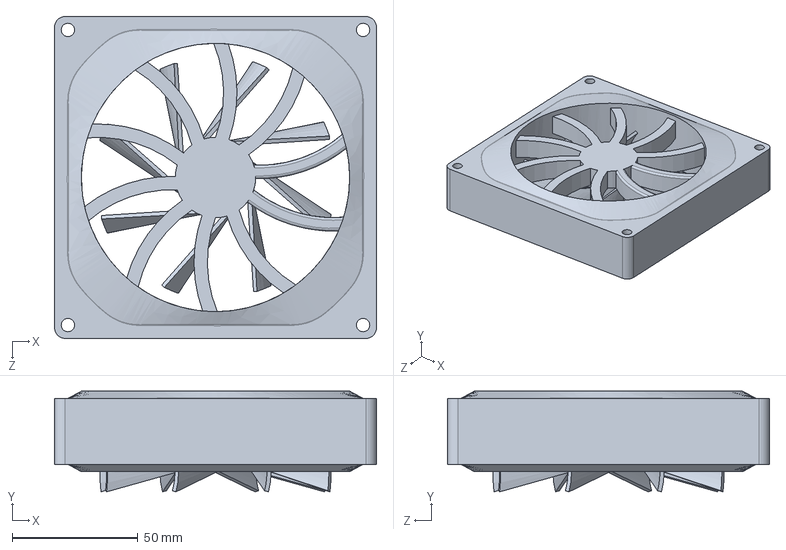
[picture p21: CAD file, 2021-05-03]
Chassis/3d/Assembly - FULL/Fan.SLDPRT
128.0 x 40.0 x 128.0 mm

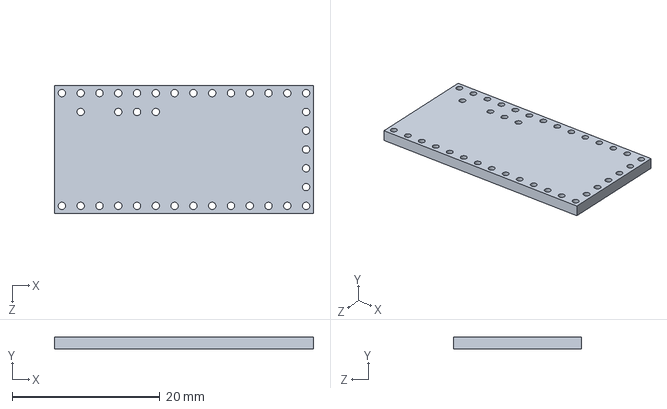
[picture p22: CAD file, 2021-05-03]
Chassis/3d/CaseAssembly/Teensy 3.1 PCB.SLDPRT
35.0 x 1.60 x 17.2 mm

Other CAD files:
Chassis/3d/CaseAssembly/Teensy 3.1.SLDASM
Chassis/3d/CaseAssembly/FullAssembly.SLDASM
Chassis/Backplane/output-Mar-10-2021/HaHK_Box/ExportSTEP/PCardWBJ.step
Chassis/Presentation/Presentation/August 2020/HaHK_Box/ExportSTEP/PCardWBJ.step
Chassis/Presentation/Presentation/December 2020/HaHK_Box/ExportSTEP/PCardWBJ.step
Chassis/3d/Assembly - FULL/Backplane.SLDPRT
Chassis/3d/Assembly - FULL/Eurocard.SLDPRT
Chassis/3d/Assembly - FULL/PowerSupply.SLDPRT
Chassis/3d/Assembly - FULL/RackCasing.SLDPRT
Chassis/3d/Assembly - FULL/Teensy/Teensy 3.1 PCB.SLDPRT
Chassis/3d/CaseAssembly/Backplane.SLDPRT
Chassis/3d/CaseAssembly/Display.SLDPRT
Chassis/3d/CaseAssembly/Eurocard.SLDPRT
Chassis/3d/CaseAssembly/Fan.SLDPRT
Chassis/3d/CaseAssembly/PowerSupply.SLDPRT
Chassis/3d/CaseAssembly/RackCasing.SLDPRT
Chassis/Backplane/Backplane_keepOut9-2020.DXF
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

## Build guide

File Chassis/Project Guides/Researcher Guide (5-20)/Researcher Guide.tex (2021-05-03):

% The "%" character denotes a comment
\documentclass[prb,preprint]{revtex4-1}
\usepackage{amsmath}  % needed for \tfrac, \bmatrix, etc.
\usepackage{amsfonts} % needed for bold Greek, Fraktur, and blackboard bold
\usepackage{graphicx} % needed for figures

\begin{document}
\title{Researcher Guide For The H.aHKBox}
\author{Adam Stammer under the direction of Dr. Carl Ferkinhoff}
%\email{adam.stammer@go.winona.edu}

\date{\today}

%if you include an abstract, it goes here
\begin{abstract}
This document is intended to help guide future researchers in their research and development of the Hardware.astronomy: Housekeeping Box. I began working on this project in the summer of 2019, under the direction of Dr. Carl Ferkinhoff, at Winona State University. This guide summarizes some of the thought processes and plans that went into this project, the tools and softwares used in its development, and gives tips on mistakes made and lessons learned.
\end{abstract}

\maketitle
%title page ends here

\section{Overview of Project}
\subsection{History}
Carl Ferkinhoff designed and built the ZEUS Radio Spectrometer while getting his PhD in Astronomy (2014). The device itself uses non visible light frequencies to take 'pictures' of the sky. It's tempting to consider it a telescope, but technically spectrometer is a more apt title. After learning so much with the ZEUS, Carl began designing its predecessor. With the success of the ZEUS, he was able to acquire funding for the ZEUS2. The spectrometer itself is roughly a cylinder about 3' by 4', though I haven't seen it in person so I'm just guessing on the size. Specifics of the history on this remain fuzzy to me, which is why I won't go into more detail in this section. It's fun to know what led to you working on the project, but understanding this is not crucial to success in future development. I strongly suggest you ask Carl about it! I'm sure he'd love to explain it all far better than I can. You can find more information on the background of Dr. Ferkinhoff, ZEUS(2), and his other projects at the following links. \url{https://sites.google.com/site/carlferkinhoff/welcome-1} \newline \url{http://hosting.astro.cornell.edu/~spifiweb/zeus2/index.html}

\subsection{Background: Electromagnetic Interference}
It is known that everything gives off various forms of electromagnetic radiation. Some of that light falls under the spectrum that ZEUS2 captures. This means that anything that ZEUS2 looks at can interfere with the astronomical sources that ZEUS2 is concerned with. The air between ZEUS2 and the sky for example. I like to imagine taking a thermal image when it is really hot out. The air itself will make the image fuzzier and less informative, as hot physical objects just blend in with the air in the picture. Only the most hot things will actually show in the picture because they need to overcome the light given off by the air. This is one reason that astronomical observers, like spectrometers, are placed as high in altitude as conveniently possible, like on the top of a mountain. It decreases interference from the air, clouds, and the earth itself. Some of these devices even make it out into space, like the Hubble Telescope.  ZEUS2 stays on the ground but not anywhere near Winona, MN. As such, I've never seen the device in person. For a tangible demonstration of the light spectrum, I found \url{https://viewspace.org/interactives/unveiling_invisible_universe/electromagnetic_spectrum/forms_of_light} to be a big help. I think an Optics class would cover this kind of thing in depth, but as I have not taken Optics, I can't say for certain.

ZEUS2 is also an object of matter, meaning that it too gives off electromagnetic radiation. Imagine putting on a headlamp that was turned back towards yourself. It's hard to see past the bright light that you can't get away from. Thankfully this electromagnetic radiation is a result of inherent heat in the given objects. The colder they get, the less radiation they give off, and not just in infrared. This means that lifting these observation devices higher decrease interference not only because there is less stuff between the observer and the observed, but also because what is between is colder. 

\subsection{ZEUS2 Cool 4 U}
By simply cooling down ZEUS2 itself, we can limit how much it interferes with the radiation it is trying to observe. Just cold isn't good enough though. We need it really really cold. The cooler itself functions on the same principles a refrigerator cooler. Things get colder when they decompress, and warmer when they compress. So, just compress something, move the heat away (like a fan), then decompress it, and you've now cooled down that something. A refrigeration unit, will use a coolant, liquid or gas, that's usually inert so as to not cause accidental chemical reactions (Helium for example). Use the process described above to cool said coolant down, and the use the coolant to cool down something else.

A food freezer can run off of a single refrigeration unit, but that's not cold enough for ZEUS2. You would have to compress your coolant down way way too much to get it cold enough for ZEUS2. To make this process more economical, you can do it in stages. Compress, Cool, Decompress, Repeat. These are usually called Multistage Refrigeration Systems and can be implemented differently. Some have multiple compressors, one for each stage, while others just loop the coolant through a single compressor multiple times. Sometimes I like to use an oversimplified explanation for this cooler by saying it's a freezer inside of a freezer inside of a freezer.

As you can imagine, this cooling process takes time. Plug in a new refrigerator in your kitchen and it takes hours to get down to the proper temperature. Astronomical Observation sites tend to be rented out to various groups, making observation time precious and expensive. If the temperature of ZEUS2 is wrong, data can't be collected. ZEUS2 is also calibrated such that collected data is dependent on a very small window of acceptable temperatures. This means that ZEUS2 must be kept cold but not too cold, or data collection must cease until those ideal conditions are met. This is why ZEUS2 needs housekeeping equipment to control the cooler. 

\subsection{The Problem}
ZEUS2 already has equipment that accomplishes this task. It's expensive, relatively old, proprietary, and specific to tasks that fall somewhat outside the scope of ZEUS2. The equipment works, but it's far from perfect. What happens when the equipment breaks? Originally, you'd have to send the equipment into the manufacturer for repair. This takes a lot of time and costs quite a bit. To make matters worse, what do you do when the manufacturer stops supporting your equipment, or goes out of business all together? You can try to fix the device yourself, but the designs are proprietary so you'll have to do a good bit of reverse engineering, and you risk breaking the equipment worse. This also takes even more time. You can buy an entirely new device that will serve the same purpose, but you'll eventually run into the same problems with that equipment, and it's really expensive.

Along with this problem, the existing equipment was not designed for ZEUS2. It isn't even one piece equipment, but multiple separate units working together. It functions well enough for the task at hand but it's not the most efficient about it. The equipment takes up a lot of space for features that don't even apply to ZEUS2, and some features rely on workaround and hacks that are inconvenient. A result of this inefficiency is that sometimes ZEUS2 is overcooled, and operators have to wait for the device to warm back up to temp. This can waste precious observation time. 

\section{The Solution}
This is where the H.aHKBox comes in. The goal is design a single unit that can replace the existing equipment, that can not only be self repaired easily, but also leaves room for future additions. It can function not only as a the temperature monitor, but also as the cooler controller, among other things. It is a modular systems such that every functional unit can be developed as a plug-n-play circuit board. I like to think of this like plugging a Graphics Card into the Motherboard of a desktop computer. These cards can communicate together as necessary, get power from the Motherboard, and each have their own external connections that allow for hookups to external sensors and devices. This project is Open Source, to aid in future repairs, and increase implementation and design. The project is broken into 5 physical design units listed in the subsections below.

\subsection{4-wire AC Bridge}
Unknown Daughtercard.

\subsection{4-wire and 2-wire DC Bridge}
Unknown Daughtercard.

\subsection{PID Controller}
This is a daughtercard to function as a PID (Proportional-Integral-Derivative) Controller. This is a common control unit for systems that need to accurately and precisely respond to incoming data in a small amount of time. The Cruise Control of a car is an example of this. It takes in the measured the speed of the vehicle, compares this input with the user input desired speed, and outputs in a way that puts mechanical response on the engine.

This particular PID Controller Card will function as the temperature controller. It will read in from temperature sensors connected to ZEUS2, compare those temperatures to the desired values, and output to the cooler such that the proper temperatures are maintained. 

\subsection{P-Card}
Since the daughtercards need to be designed and tested but cost a small fortune to manufacture, I designed a prototyping card. It can plug into the motherboard, and uses a female connector along with banana jacks to allow for prototyping circuits on the attached breadboard. I like to call it the Jean-Luc P-card in honor of Star Trek's greatest captain, but Prototyping-card works too. Once this is complete, prototyping the cards listed above should be much easier.

\subsection{Chassis}
This is foundation of the unit. It consists of the case itself, power supplies, cooling fan, touch screen, motherboard/backplane, micro-controllers (Arduino Uno, Raspberry Pi), and port panel. The chassis does not perform any functions without cards installed. It's not a perfect analogy, but you can imagine a desktop computer without a cpu or gpu. It is the foundation for the device, but it is relatively useless alone. This is where most design time has been invested so far, but fleshing out the P-card really helped flesh out what the connectors needed to look like on the backplane. I have not done much in regards to physical or mechanical design. I've been almost exclusively doing electrical design with heavy plannings towards the software design.

\subsection{Knowledge "Requirements"}
Astronomy is cool! Carl knows it and he'll do everything to help you understand it too! Don't ever shy away from learning something new, astronomy related or not. That said, this project tends to fall under mechanical, electrical, and software engineering, with significant standing in control theory. I mean this with lots of love: this project is essentially a glorified thermostat. To do it right you're going to want to understand the basics of how astronomy is done, but you don't need an astronomy degree. You'll learn a lot more than you need to, and not just in astronomy, which is really cool! Yes, you are here to work on this project, but you're also here to learn and have fun! If something peaks your interest and it will help you accomplish a task, spend some time to learn more about it.

\section{What We've Accomplished}
\subsection{Case}
The case to be used was picked out quite a while ago, but I don't remember exactly which one. There should be documentation in OSF regarding the case selection. The 3D renders are where I'd start looking.

\subsection{Power Supplies}
After a lot research and consideration regarding the desired capabilities of the H.aHKBox, we decided to have two separate power supplies: One 24V 350W, One 5V 110W. The goals here is that each card would run around 10W max, but one or two cards could run at a higher power. Just had the idea of adding a ammeter to each supply which could report to the screen.

\subsection{Touch Screen}
We chose a touchscreen designed specifically for the Raspberry Pi. It allows for the Raspberry Pi to be mounted to the back of it which helps efficiently use the space inside the case. It's 7" and uses HDMI and USB to connect to the Pi.

\subsection{Motherboard/Backplane}
With 10 card slots, 3 temperature sensors, arduino hookup, 7-segment display output, and connectors for data and power, the electrical design for this board is well under way.

\subsection{P-Card}
The design for this card is finished, but translating that into electrical designs that can be sent to a manufacturer have proven difficult. I'm very close to being finished with it though. My first mistake was designing the entire thing backwards. In order for it to plug into the motherboard it would've been upside-down. Tried to fix it but then it was upside-down the other way. Tried to fix it again and that's where I am now. Still need to route some connections and then hopefully I finally got it right.

\subsection{Microcontrollers}
We did choose the Arduino Uno and Raspberry Pi Model 3 B+ to act as the brains of the Motherboard. They're well documented and have the communication features I sought.

\section{What Still Needs To Be Done}
\subsection{Card Design}
The Bridge Cards mentioned above have not been started on as far as I'm aware. Designs for the Motherboard are fleshed out enough at this point that someone could begin working on those cards. 

\subsection{P-Card}
The P-card design is so close to being done. Hopefully within the first week or two work this summer we'll be able to order the cards from a manufacturer.

\subsection{Motherboard/Backplane}
Designs of the Motherboard still need to be finished. The limited space has already proven to be a challenge, but it shouldn't be too big of a problem. Running traces for this board is going to be a real challenge, but it should be fun too.

\subsection{Programming}
Once the Motherboard designs are finished the microcontrollers can be programmed. I've been looking forward to this since I started working on this project. It'll be a fun balancing act of low level communication protocols.

\subsection{Port Panel}
External devices need to be able to connect to the H.aHKBox and this panel will act as a the connection converts so that wires are able to plug in. This is probably the last thing that will happen since its design depends on not only all the other designs but also on what external devices will be used and what connectors they use.

\section{Common Tools}
The tools used in this project are to some degree personal preference. If it works, that's good enough. That said, some things make a lot more sense than alternatives even if you have to learn a new program. This project is a fantastic opportunity to learn new softwares, especially since the university gives students access to professional softwares that are desirable to add to your resume. One of my coworkers last year learned SolidWorks from scratch and is now comfortable enough to add it to her resume. I myself knew very little about digital circuit design, but now I'm relatively fluent with CircuitMaker. Below I'll list the software I used and what I used it for, but you can always make a case for something else.

\subsection{CircuitMaker}
I spent most of my time in this software. It is touchy and has a lot of bugs, but it's free which is nice. it's also quite similar to the professional software Altium which is used by many companies. I'm sure the knowledge and experience I've gained on this software would carry over to Altium quite well. My biggest suggestion here is to use a mouse, not a trackpad, whenever possible. The zoom functions don't work properly with a trackpad, so I pretty much always had a USB mouse with me, or used my Desktop PC. Also, this software is not that lightweight. It's not easy to run and the more complex your project, the slower everything goes. All the more reason why I used my Desktop whenever possible. The WSU issued laptops can do it, but only barely. 

I also found the tutorials to be outdated as the interface has changed since the tutorials were developed. The Altium forums were extremely helpful in debugging things as most problems I ran into someone else had run into before me. Even still there were some bugs that I just never did figure out. Some went away on their own, others didn't. When in doubt, restart the application. Save your work as often as you can. It's easy to get lost in the flow of work and then have the program crash and you just wasted two hours. I'm not proud but that happened to me more than once.

\subsection{OSF}
Open Science Foundation is where we document our work. It provides a centralized location for all documents regarding Hardware.astronomy projects. It has automatic backups, funding for like a hundred years so our data will never get lost to lack of funding, and allows us to open our research up to the public when we're done. You can upload files and type up your own pages with pictures and the like. You can use plain text typing or a simplified version of LaTeX when typing directly in OSF. This is where you're going to find all of the previously done research. It tends to be a little slow to load, which is a pain, but all in all it's not bad. Right now, the OSF page for the H.aHKBox is really unorganized and it's hard to find what you need. I'll probably spend some time really soon cleaning everything up.

You also have a personal page for file uploads and documents typing. I used this a bit for planning the project, like a to-do list for the day/week and solidifying my long term goals with dates. Mostly, though, I wrote daily reports. I'd start the day by typing out a short paragraph about what I wanted to accomplish that day. Then I'd end the day by typing out what I did and how it related to that goal. I wasn't directly tracking my "success" at staying on task, but putting it into words certainly helped me get started each day, and decide what to do the next day.

\subsection{SolidWorks}
I didn't have to use SolidWorks that much because I wasn't doing any mechanical design. I'm also not an expert at using the software. I have used Blender, Maya, and 3DS before and I can say with confidence that SolidWorks is easier to use, especially when it comes to mechanical design like this. The tutorials I followed were pretty good, and what few problems I ever had were easily solved with a google search. Again, I suggest a mouse over a trackpad.

\subsection{Git and Github}
If you've never used github, this could be a fun excuse to do so. If you have any intention of working in software in the future I strongly suggest you learn how to use it. There are a lot of tutorials out there and a lot of different ways to do it. I prefer using git for my file hosting over OSF just because it's so much faster for me to do that. I even use github for all of my school stuff like homework. It allows me to easily transition from laptop to desktop and back.

I use the commandline git tool, not the GUI, so I can't help much if you use the GUI. I haven't used git with multiple people on the same project in the better part of a decade so if you are interested in that, it'll be a learning experience for both of us. I know I need to figure out how to do that soon enough anyway. I am currently the owner of the git repository for this project, so if you have any interest in using it too just let me know and I'll look into a better setup for multiple people.

Github does link into OSF really well so if you don't have any interest in git, you can still access all of the files I put there through OSF. I update git multiple times a day but tend to only transition it to OSF itself when I hit major checkpoints. If you need my most up to date version of something that I've been working on very recently, you should probably check git first unless you specifically ask for me to update the OSF version.

\subsection{Whiteboard}
I know this may be meaningless with COVID19 keeping everyone inside, but a large whiteboard is so so helpful. I'm sure paper sketching is a fine substitute but after working on this project I decided I'm definitely getting a whiteboard for my room.

\subsection{Coworkers}
We all know different stuff to different degrees. We can all lean on each other and it only increases the fun to share knowledge. The only thing I love more than teaching others is learning from others. You need help with something, just ask. If not me someone else. If I don't know the answer I'll likely help you find it. That said, don't assume I'm always right. We all make mistakes. Stay vigilant of that and you'll do great!

\subsection{Email}
Emails aren't a bad way to communicate, especially if someone is currently unavailable by other means. I check mine regularly and you should do the same, especially working from home. I generally set aside 15 minutes after lunch to check it and respond to stuff as necessary. This also helps keep me in the mindset of work.

\subsection{Microsoft Teams}
I've never used Teams before. Last summer we used Slack but it wasn't the most cooperative. Hopefully Teams will be a little more seamless.

\subsection{Discord}
I use discord for a lot of different things so I pretty much always have it going if I'm at my computer. I'll be making a discord channel specifically for this research group once we get started and it's my preferred method of contact. Instant messages are great if it's a simple question and voice calls are a good backup for more in depth conversations. Zoom and Teams could be used instead, but I think they're both a bit more of a hassle to use. It is all up to personal preference though.

\section{Workflow}

\subsection{Routine - Personal Notes}
I suggest you use this as an opportunity to setup a daily routine. I'm sure Carl will talk to everyone about it, but it's good to build habits around work, especially when your place of work is not just your place of work. I use my gaming PC to work on this project, which means getting in the proper mindset of working each morning is really important. Carl will definitely cover some basics of how to do this but I start off by looking at my "to-do list". I use a website called Trello for this but you can use plenty of different things. If you do use something like this make sure it's linked somehow to OSF. Just a link in your personal notes would suffice. After checking that I write up a daily task list. This is usually a paragraph of explaining what I want to do today and why, followed by a checkbox list of tangible tasks. This I do entirely on OSF with a new personal wiki page for each month. This was entirely Carl's idea (and it was a huge help) so I'm sure he'll go over it in more detail than this. I finish up the day in the opposite order. Fill in the checkbox list as needed, write up a summary for the day and a short idea of what to start the day with tomorrow. Then update the to-do list if necessary. This "sandwich" of preparation and summary really helps me stay in the mindset of working and stay on task.

\subsection{Group Meetings}
Look through some of the group meeting notes on OSF. It can be a little daunting sometimes but please take advantage of the meetings. Ask questions if you have them. Share your successes and failures with everyone. It can not only help you get past hurdles in your research but really helps get over any presentation anxiety regarding your project. It takes time for the project to really feel like your own and these meetings give you a chance to show off what you did, which really really helps.

%\begin{thebibliography}{99}
% The numeral (here 99) in curly braces is nominally the number of entries in
% the bibliography. It's supposed to affect the amount of space around the
% numerical labels, so only the number of digits should matter--and even that
% seems to make no discernible difference.
%Not Requested
%\end{thebibliography}

\end{document}

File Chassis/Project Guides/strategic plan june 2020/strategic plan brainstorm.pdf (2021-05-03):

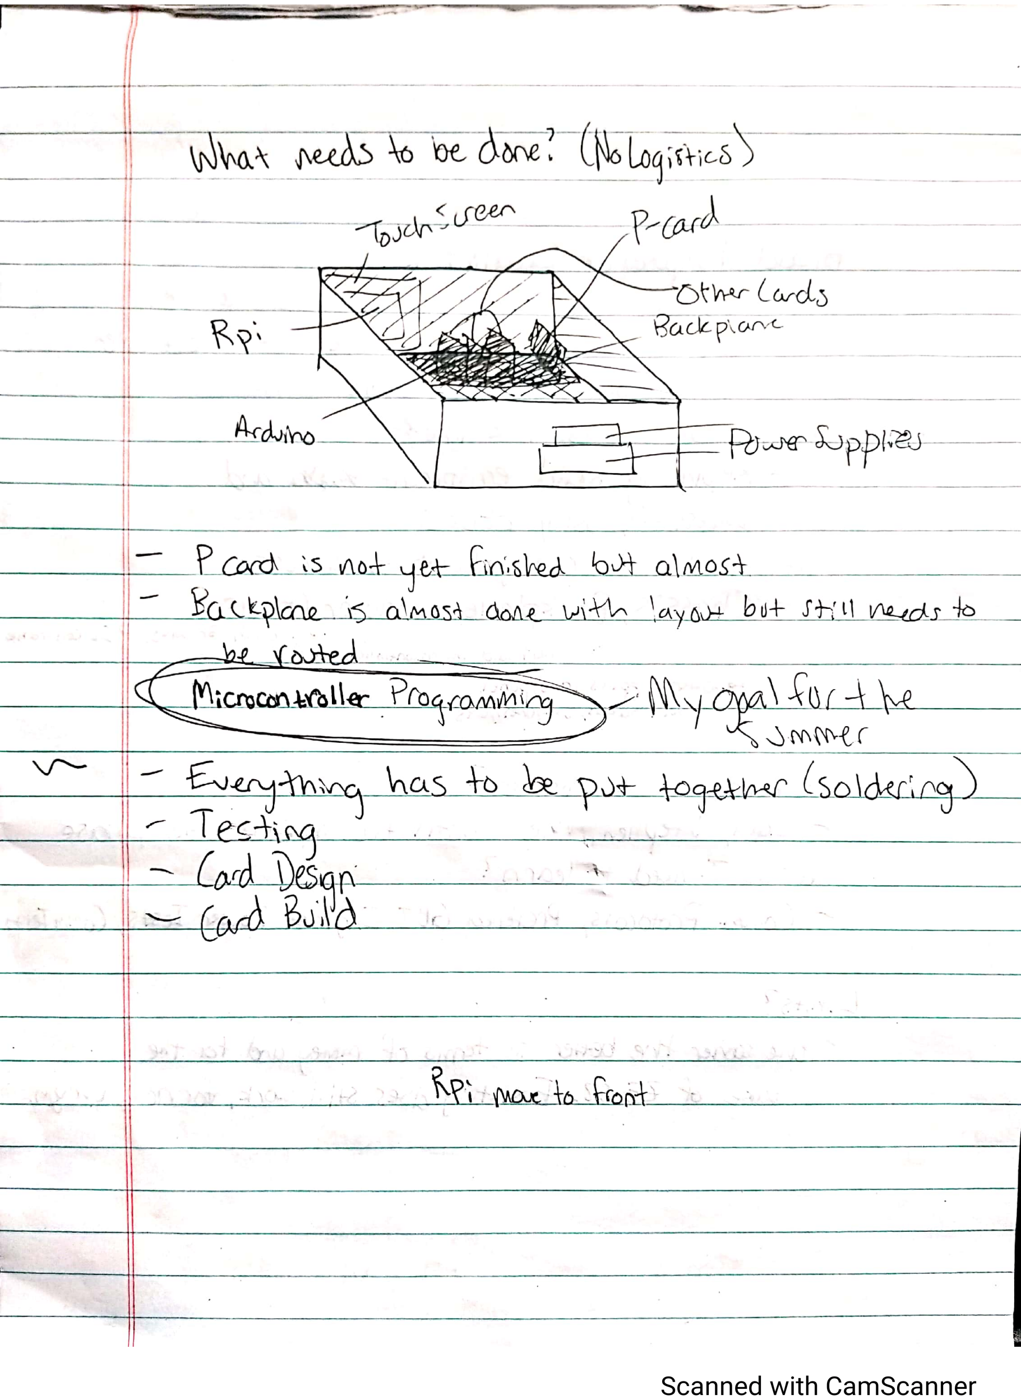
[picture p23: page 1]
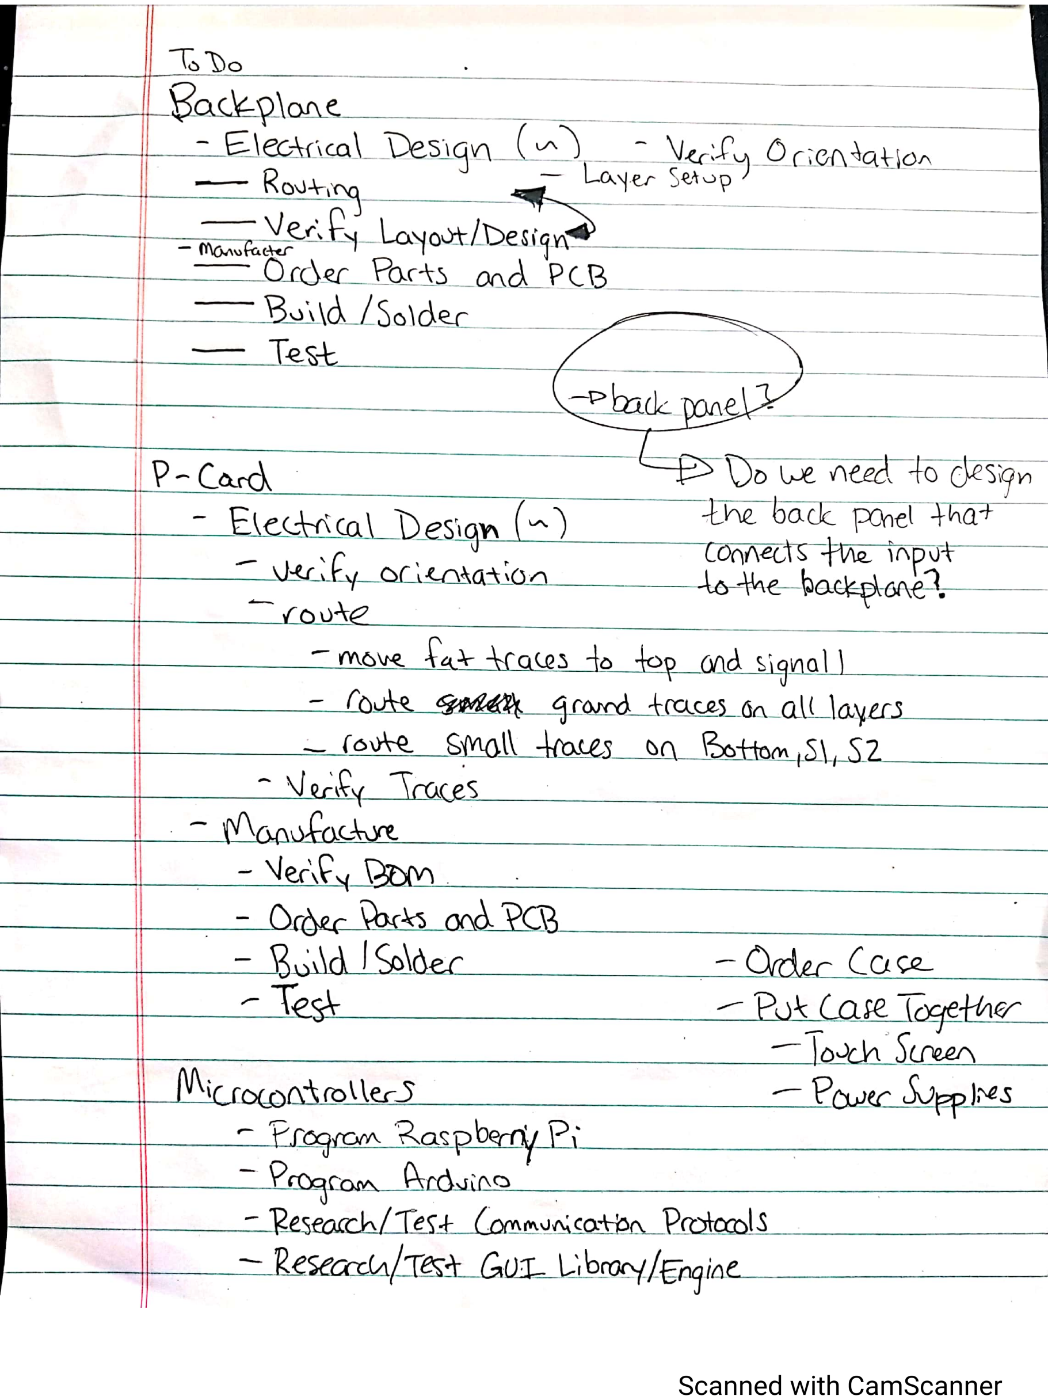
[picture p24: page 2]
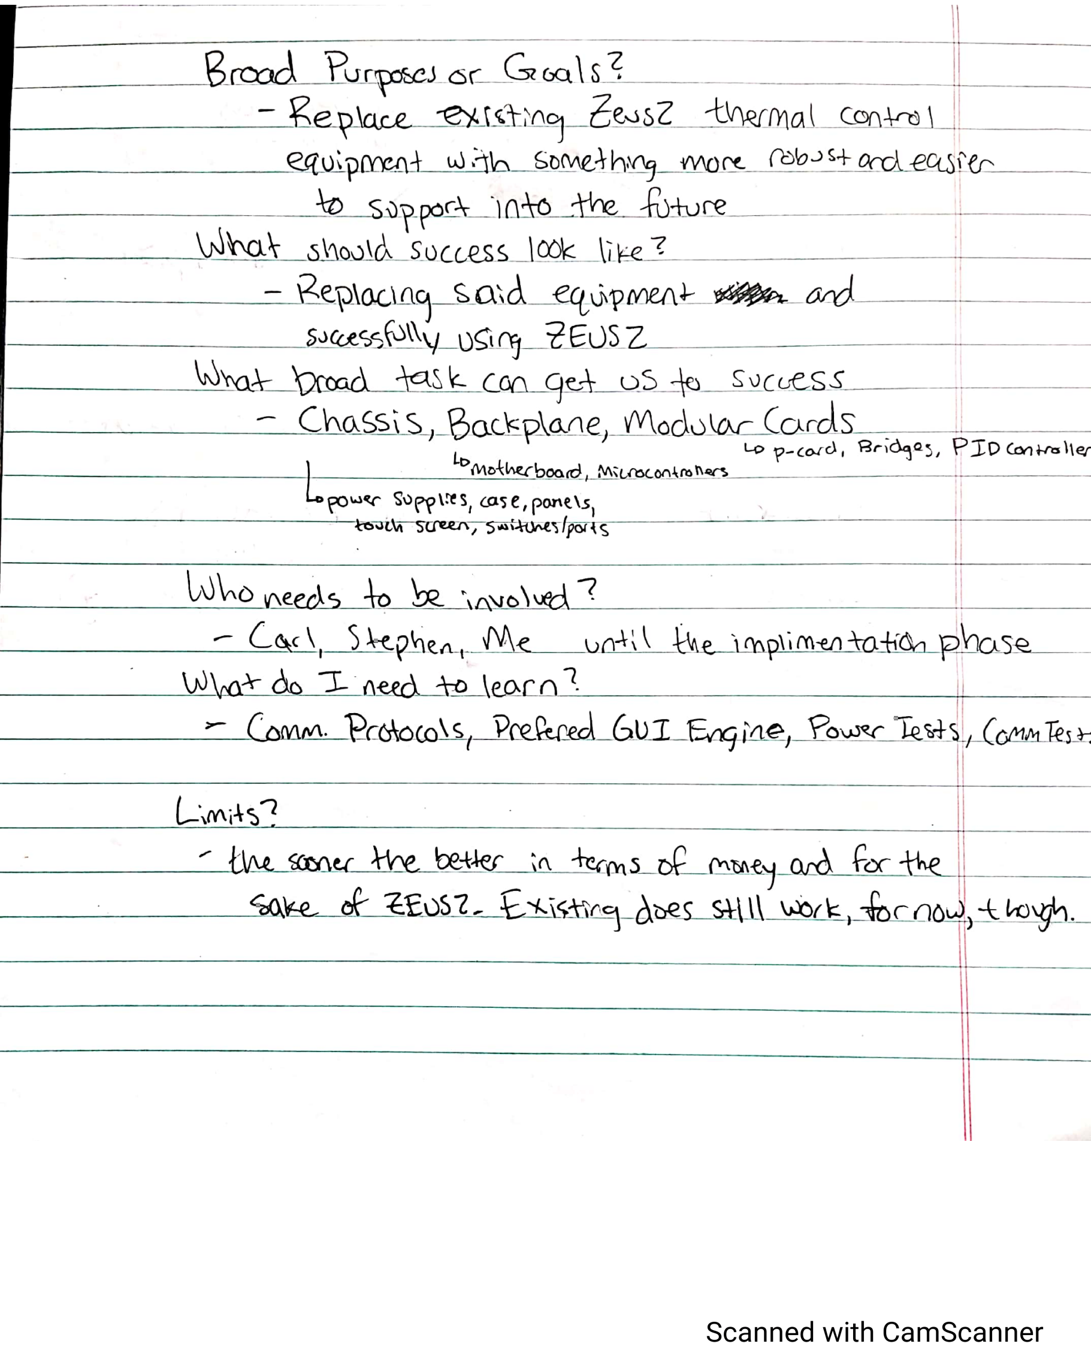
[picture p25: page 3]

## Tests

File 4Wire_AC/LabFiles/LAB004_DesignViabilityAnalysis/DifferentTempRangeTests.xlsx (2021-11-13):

100k Ohms R_ref (clipped around 9.3k Ohms)
GRT Value (k Ohms) | 9.3 | 9 | 8.5 | 8 | 7.5 | 7 | 6.5 | 6 | 5.5 | 5 | 4.5 | 4 | 3.5 | 3 | 2.5 | 2 | 1.5 | 1 | 0.5
Voltage Amplitude (mV) | 2821 | 2707 | 2526 | 2346 | 2162 | 1984 | 1800 | 1616 | 1437 | 1264 | 1090 | 920 | 756 | 600 | 452 | 315 | 195 | 95 | 25

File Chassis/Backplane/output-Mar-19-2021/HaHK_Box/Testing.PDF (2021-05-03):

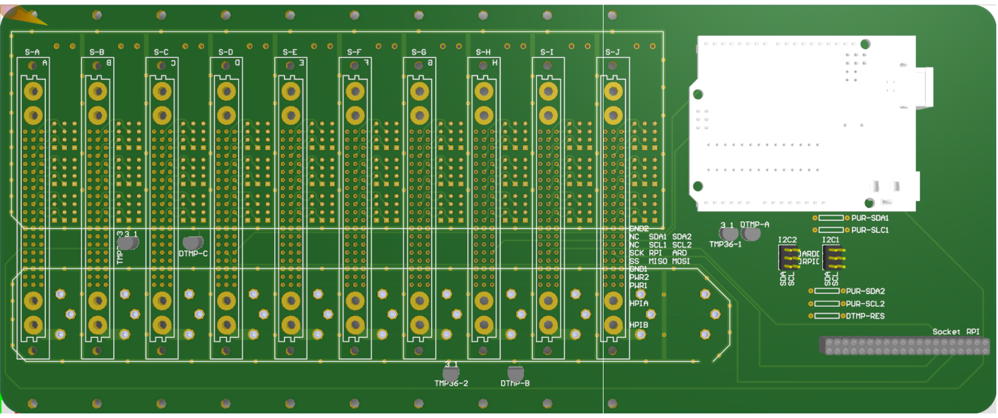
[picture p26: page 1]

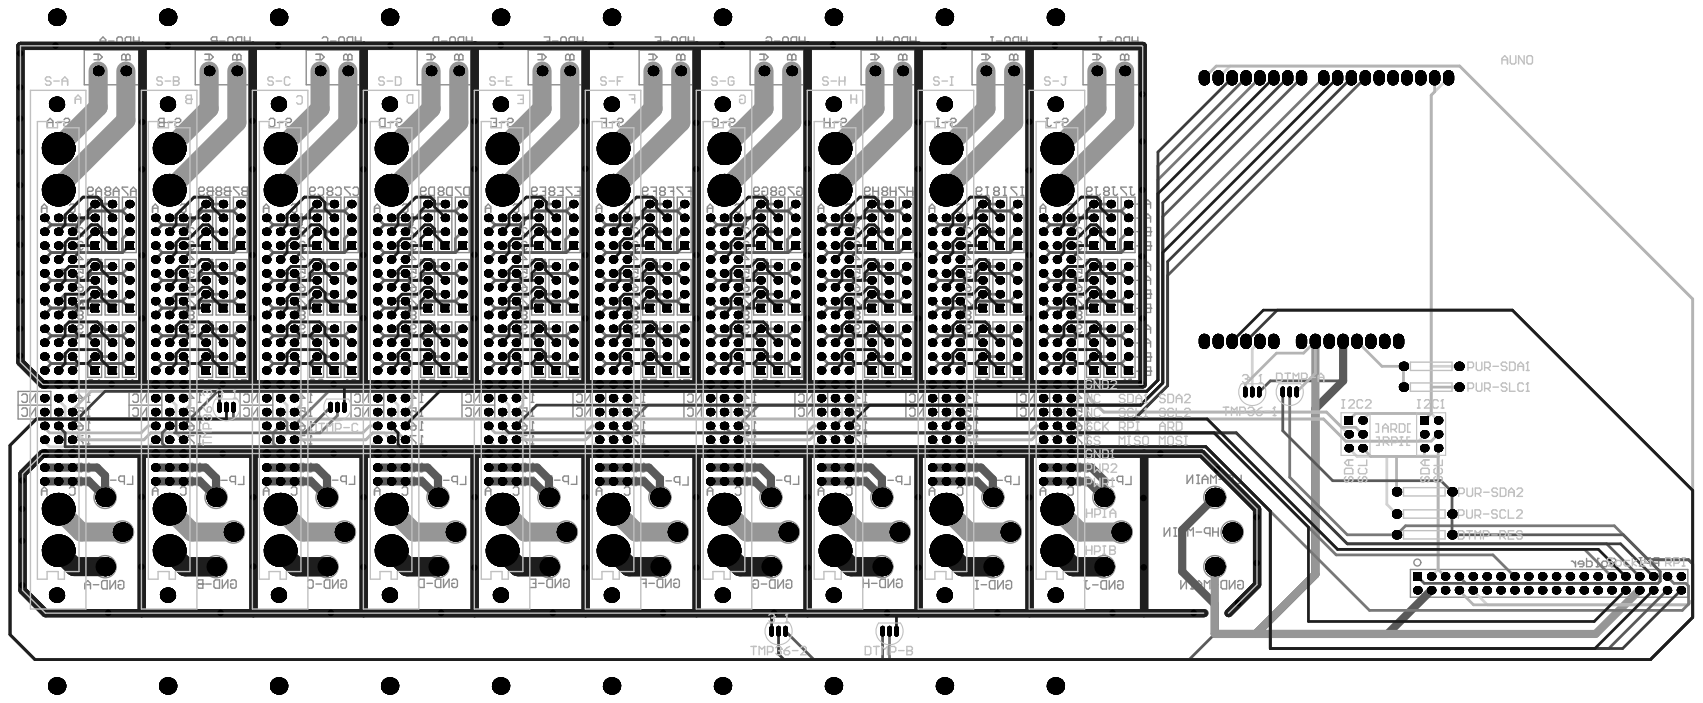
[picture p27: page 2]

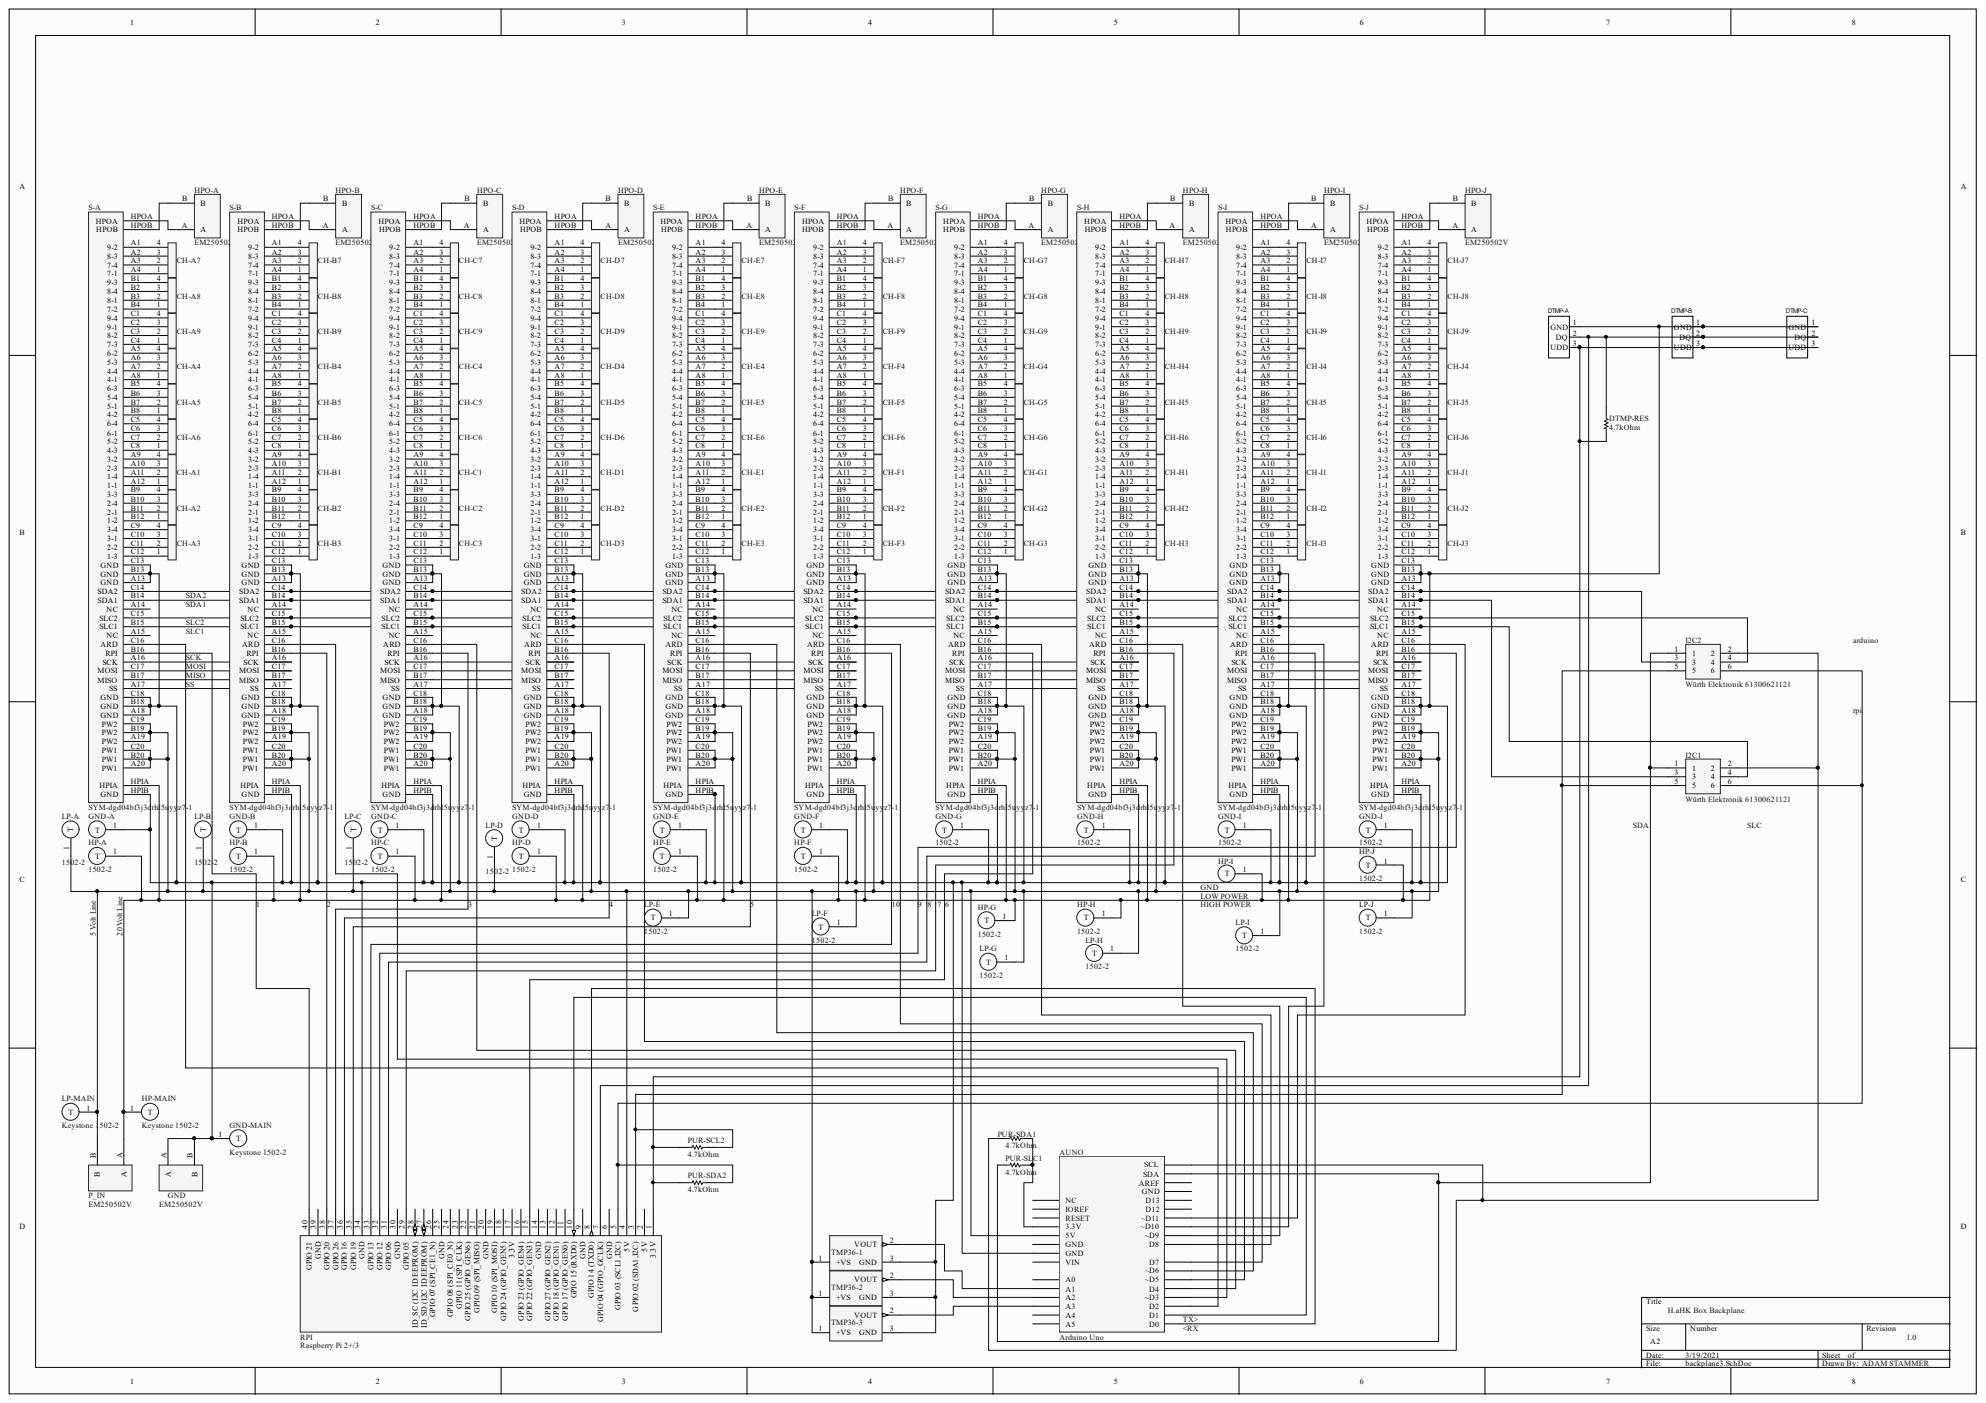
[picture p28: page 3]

SLC1 | PW1 | A20 PW1 B20 PW1 C20 PW2 A19 PW2 B19 PW2 C19 GND A18 GND B18 GND C18 SS A17 MISO B17 MOSI C17 SCK A16 RPI B16 ARD C16 NC A15 SLC1 B15 SLC2 C15 NC A14 SDA1 B14 SDA2 C14 GND A13 GND B13 GND C13 | PW1 | A20 PW1 B20 PW1 C20 PW2 A19 PW2 B19 PW2 C19 GND A18 GND B18 GND C18 SS A17 MISO B17 MOSI C17 SCK A16 RPI B16 ARD C16 NC A15 SLC1 B15 SLC2 C15 NC A14 SDA1 B14 SDA2 C14 GND A13 GND B13 GND C13 | PW1 | A20 PW1 B20 PW1 C20 PW2 A19 PW2 B19 PW2 C19 GND A18 GND B18 GND C18 SS A17 MISO B17 MOSI C17 SCK A16 RPI B16 ARD C16 NC A15 SLC1 B15 SLC2 C15 NC A14 SDA1 B14 SDA2 C14 GND A13 GND B13 GND C13 | PW1 | A20 PW1 B20 PW1 C20 PW2 A19 PW2 B19 PW2 C19 GND A18 GND B18 GND C18 SS A17 MISO B17 MOSI C17 SCK A16 RPI B16 ARD C16 NC A15 SLC1 B15 SLC2 C15 NC A14 SDA1 B14 SDA2 C14 GND A13 GND B13 GND C13 | PW1 | A20 PW1 B20 PW1 C20 PW2 A19 PW2 B19 PW2 C19 GND A18 GND B18 GND C18 SS A17 MISO B17 MOSI C17 SCK A16 RPI B16 ARD C16 NC A15 SLC1 B15 SLC2 C15 NC A14 SDA1 B14 SDA2 C14 GND A13 GND B13 GND C13 | PW1 | A20 PW1 B20 PW1 C20 PW2 A19 PW2 B19 PW2 C19 GND A18 GND B18 GND C18 SS A17 MISO B17 MOSI C17 SCK A16 RPI B16 ARD C16 NC A15 SLC1 B15 SLC2 C15 NC A14 SDA1 B14 SDA2 C14 GND A13 GND B13 GND C13 | PW1 | A20 PW1 B20 PW1 C20 PW2 A19 PW2 B19 PW2 C19 GND A18 GND B18 GND C18 SS A17 MISO B17 MOSI C17 SCK A16 RPI B16 ARD C16 NC A15 SLC1 B15 SLC2 C15 NC A14 SDA1 B14 SDA2 C14 GND A13 GND B13 GND C13 | PW1 | A20 PW1 B20 PW1 C20 PW2 A19 PW2 B19 PW2 C19 GND A18 GND B18 GND C18 SS A17 MISO B17 MOSI C17 SCK A16 RPI B16 ARD C16 NC A15 SLC1 B15 SLC2 C15 NC A14 SDA1 B14 SDA2 C14 GND A13 GND B13 GND C13 | PW1 | A20 PW1 B20 PW1 C20 PW2 A19 PW2 B19 PW2 C19 GND A18 GND B18 GND C18 SS A17 MISO B17 MOSI C17 SCK A16 RPI B16 ARD C16 NC A15 SLC1 B15 SLC2 C15 NC A14 SDA1 B14 SDA2 C14 GND A13 GND B13 GND C13

SDA2
SDA1

SLC2 | | | | | | | | | | | | | | | | | | | I2C2

MOSI
MISO | Würth Elektronik 61300621121 | rpi
SS

HP-J T 1
HP-I

GND-MAIN | | PUR-SDA1

PUR-SCL2 | | 4.7kOhm | AUNO

IOREF D12 RESET ~D11 3.3V ~D10 5V ~D9 GND D8 GND VIN D7 ~D6 A0 ~D5 A1 D4 A2 ~D3 A3 D2

3.3V 1 5V 2 GPIO 02 (SDA1,I2C) 3 5V 4 GPIO 03 (SCL1,I2C) 5 GND 6 GPIO 04 (GPIO_GCLK) 7 GPIO 14 (TXD0) 8 GND 9 GPIO 15 (RXD0) 10 GPIO 17 (GPIO_GEN0) 11 GPIO 18 (GPIO_GEN1) 12 GPIO 27 (GPIO_GEN2) 13 GND 14 GPIO 22 (GPIO_GEN3) 15 GPIO 23 (GPIO_GEN4) 16 3.3V 17 GPIO 24 (GPIO_GEN5) 18 GPIO 10 (SPI_MOSI) 19 GND 20 GPIO 09 (SPI_MISO) 21 GPIO 25 (GPIO_GEN6) 22 GPIO 11 (SPI_CLK) 23 GPIO 08 (SPI_CE0_N) 24 GND 25 GPIO 07 (SPI_CE1_N) 26 ID_SD (I2C ID EEPROM) 27 ID_SC (I2C ID EEPROM) 28 GPIO 05 29 GND 30 GPIO 06 31 GPIO 12 32 GPIO 13 33 GND 34 GPIO 19 35 GPIO 16 36 GPIO 26 37 GPIO 20 38 GND 39 GPIO 21 40 RPI

GND +VS 1 | 3 TMP36-3
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

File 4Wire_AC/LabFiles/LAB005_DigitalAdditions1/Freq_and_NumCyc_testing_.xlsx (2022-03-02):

 | Num cycles | 8
 | Running sine wave from AD2 at 1V amplitude rectified
 | Using 16 bit ADC
 | Data was obtained through less cycles than intended…
Num Cycles: | 8 | 8 | 8 | 8 | 8 | 10 | 10 | 10 | 10 | 10 | 15 | 15 | 15 | 15 | 15 | 20 | 20 | 20 | 20 | 20
Frequency: | 43 | 86 | 172 | 215 | 430 | 43 | 86 | 172 | 215 | 430 | 43 | 86 | 172 | 215 | 430 | 43 | 86 | 172 | 215 | 430
RMS Readings | 0.727862 | 0.720139 | 0.693336 | 0.706083 | 0.650001 | 0.723233 | 0.712081 | 0.702817 | 0.700213 | 0.647978 | 0.727672 | 0.716597 | 0.702503 | 0.678765 | 0.652995 | 0.722811 | 0.722678 | 0.697788 | 0.689968 | 0.658677
 | 0.721596 | 0.718269 | 0.686672 | 0.664919 | 0.653932 | 0.722529 | 0.719181 | 0.696322 | 0.681377 | 0.671258 | 0.72442 | 0.718825 | 0.695345 | 0.692842 | 0.662714 | 0.722954 | 0.721538 | 0.700246 | 0.692174 | 0.65852
 | 0.71989 | 0.709482 | 0.700981 | 0.673658 | 0.663681 | 0.722469 | 0.71862 | 0.698782 | 0.705438 | 0.648999 | 0.722675 | 0.718035 | 0.700829 | 0.701046 | 0.663719 | 0.725196 | 0.717547 | 0.698075 | 0.69121 | 0.659942
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

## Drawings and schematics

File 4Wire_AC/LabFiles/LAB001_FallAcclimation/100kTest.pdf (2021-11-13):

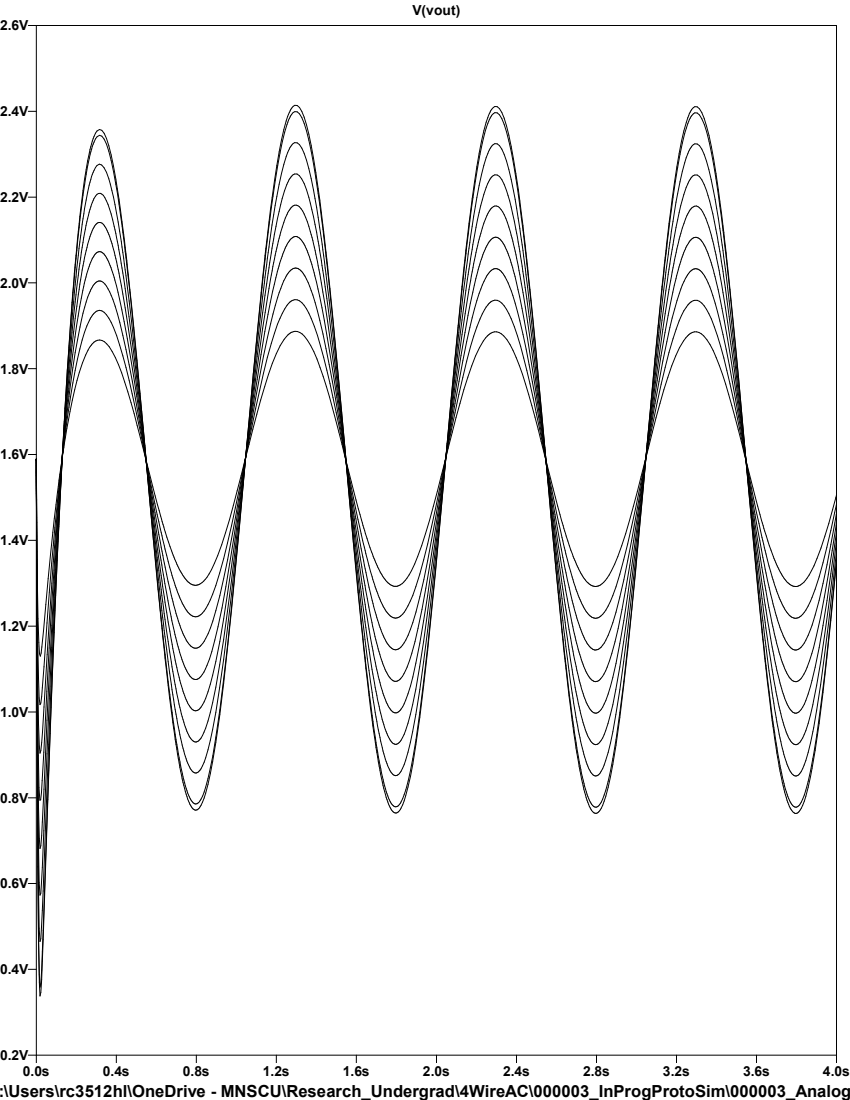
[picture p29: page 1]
V(vout)

--- C:\Users\rc3512hl\OneDrive - MNSCU\Research_Undergrad\4WireAC\000003_InProgProtoSim\000003_Analog.raw ---

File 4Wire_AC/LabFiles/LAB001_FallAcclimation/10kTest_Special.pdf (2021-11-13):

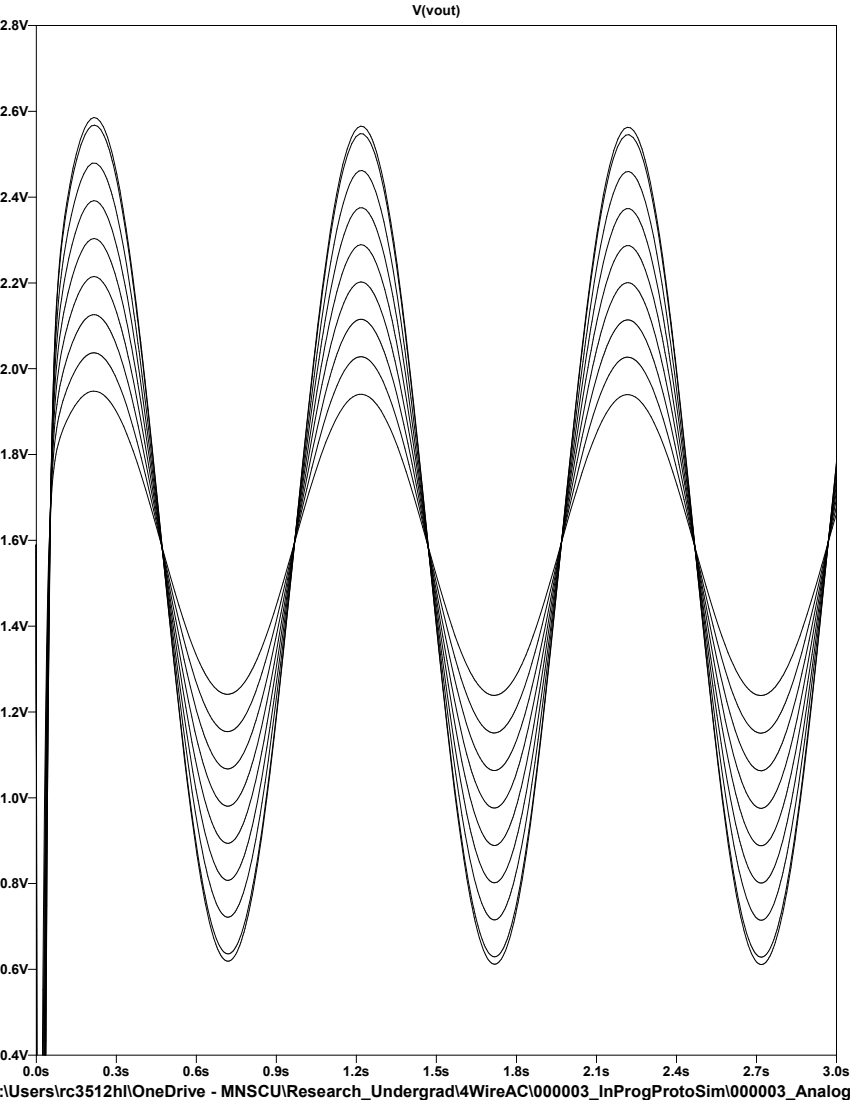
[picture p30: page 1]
V(vout)

--- C:\Users\rc3512hl\OneDrive - MNSCU\Research_Undergrad\4WireAC\000003_InProgProtoSim\000003_Analog.raw ---

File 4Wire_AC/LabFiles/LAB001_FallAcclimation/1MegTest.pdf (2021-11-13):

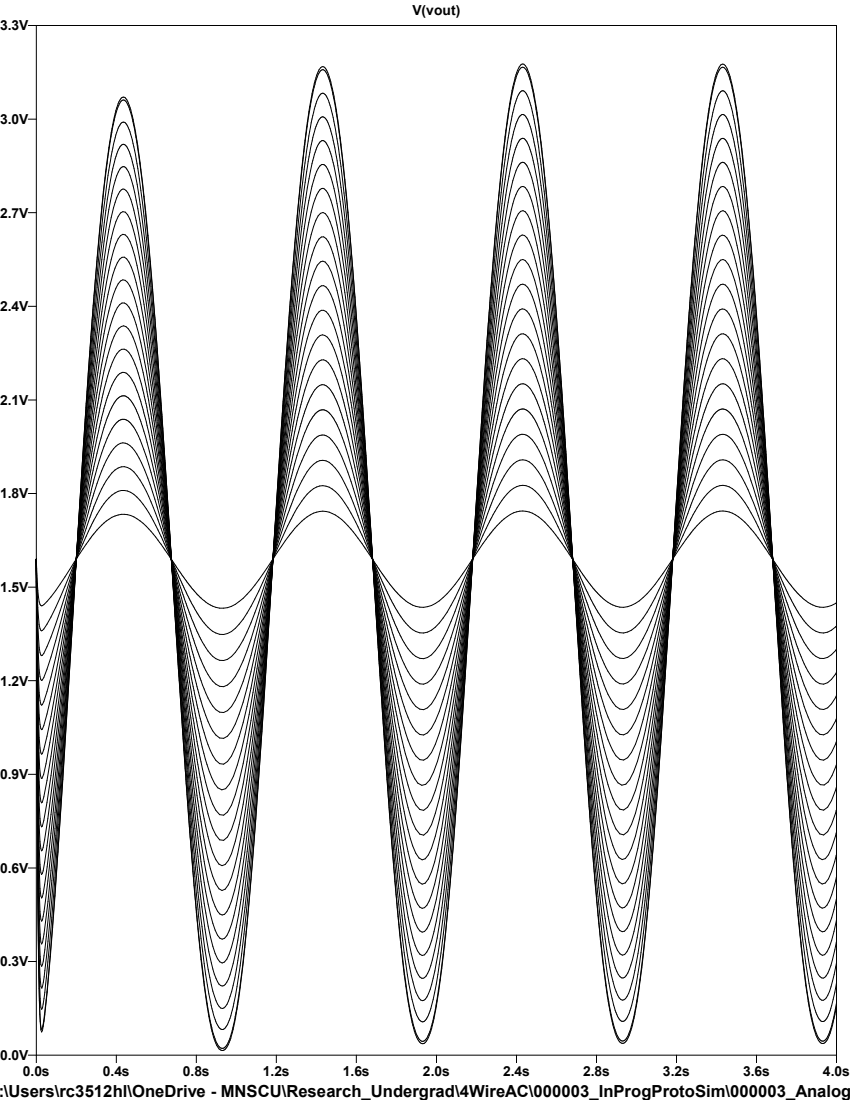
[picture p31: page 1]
V(vout)

--- C:\Users\rc3512hl\OneDrive - MNSCU\Research_Undergrad\4WireAC\000003_InProgProtoSim\000003_Analog.raw ---

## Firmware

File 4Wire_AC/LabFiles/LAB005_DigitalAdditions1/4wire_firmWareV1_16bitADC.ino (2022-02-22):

/*
   4-wire Firmware
   WAG _ Project H.aHK Box _ 4-wire AC Daugter Card
   Version 1.1
   S. Shaw
   2/13/2022

   Outputs a sine wave with user defined frequency to Teensy DAC hardware
   Calculates and outputs an RMS Voltage value at a user defined Read_Out_Rate
*/

// User Inputs
float freq_sin = 10; // Frequency of Sine Wave Modulation (Hz), [1, 160] range allowed given Nyquist sampling rate of 2 samples per period, 320 max SPS of ADC
int Num_Cycles = 10; // integer used for # of cycles per read window or the Read Out Rate.

// preset/calcuated values
float rms_sum, tim; //rms sum for RMS calculations, tim for outputting sinwave based on time
int frame; //integer used to keep track of what frame in a given window the current reading is
float period = 1 / freq_sin; // Calculate period of sine wave
int window_length = (period * Num_Cycles) / 0.0061; //integer calculated to provide the # of frames, or readings, that will be used per RMS calculation (SPS/Read Out Rate)
float twopi = 3.14159 * 2; //For sin wave generation
int tim_old = 0;

// Imports ADC library and defines hardware-to-software definition for library
#include<ADS1115_WE.h>
#include<Wire.h>
#define I2C_ADDRESS 0x48
ADS1115_WE adc = ADS1115_WE(I2C_ADDRESS);


void setup() {
  analogWriteResolution(12); //Define DAC output pin for sin wave generation
  Wire.begin();
  Serial.begin(115200); //Begin serial comm for debug
  while ( !Serial ) ; //Wait for serial comm to initialize
  // Error handling if ADC not found. Might need to run nauStartupCode or check wiring
  if (!adc.init()) {
    Serial.println("ADS1115 not connected!");
  }

  // Define ADC settings
  adc.setVoltageRange_mV(ADS1115_RANGE_4096); //comment line/change parameter to change range
  adc.setCompareChannels(ADS1115_COMP_0_GND); //comment line/change parameter to change channel
  adc.setConvRate(ADS1115_860_SPS); //uncomment if you want to change the default
  adc.setMeasureMode(ADS1115_CONTINUOUS); //comment line/change parameter to change mode

  // set dynamic variable starting values
  rms_sum = 0;
  frame = 1;
  Serial.println("");
  Serial.println(window_length);
  Serial.println("Window Length ^^");
  Serial.println("");
}






void loop() {

  /*
    // prototype code: delay until we are at wave peak
    tim = micros(); //Calculate microseconds
    // If current time is not lined up approximatly at 1/4 the sine wave, or with the first peak of a cycle, delay until alligned
    if ((int(tim) % int(period * 1000000)) > (period * 250100) | (int(tim) % int(period * 1000000)) < (period * 249900)) {
      delayMicroseconds(int(period * 1000000) - (int(tim) % int(period * 1000000)) + period * 250000);
      //Serial.print("Wait!!!!");
    }
    //tim = micros();
    //Serial.println(int(tim) % int(period * 1000000));
  */

  tim = micros() / 1000000.0; //Calculate Seconds
  Sin(freq_sin, tim, period); // Run next sinwave output voltage level based on frequency and time
  if ((tim * 1000000) - tim_old >= 6100) //trying to get to 6100 microseconds or 6.100 millis between readings
  {
    if (frame <= window_length)
    {
      rms_sum = rms_sum + sq(readChannel(ADS1115_COMP_0_GND));
      frame = frame + 1; // Update frame # for next ADC measurement
      //Serial.println(tim, 6);
      //Serial.println((nau.read() / 8388608.0) * 2.5);
    }

    else if (frame > window_length) {
      //Calculate final RMS value and output
      float rms_volt = sqrt(rms_sum / window_length);
      Serial.println("RMS_Voltage");
      Serial.println("");
      Serial.println(rms_volt, 6);
      Serial.println("");
      //Serial.print(tim, 7);
      //Serial.println("");

      rms_sum = 0;
      frame = 1; //reinitialize frame integer to 0 for next window of measurements/ next RMS value
    }
    tim_old = micros();
  }

}



float readChannel(ADS1115_MUX channel) {
  float voltage = 0.0;
  adc.setCompareChannels(channel);
  voltage = adc.getResult_V(); // alternative: getResult_mV for Millivolt
  return voltage;
}



// Sine Wave Generator Code function: Uses a table of 1024 sine wave values from [0, 1] as ratios for computing correct DAC output.

void Sin(float freq_m, float tim, float period) {
  //Full resolution is 4095, over 3.3 V -> 0.00080586 V per bit
  // Currently set to 500mV amplitude, 2V offset

  float window_tim = int(tim * 100000) % int(period * 100000); // window time in us
  float sin_values[] = {0.000000, 0.006142, 0.012284, 0.018425, 0.024565, 0.030705, 0.036843, 0.042980, 0.049116, 0.055249, 0.061381, 0.067510, 0.073636, 0.079760, 0.085881, 0.091999, 0.098113,
                        0.104223, 0.110330, 0.116432, 0.122530, 0.128623, 0.134712, 0.140795, 0.146873, 0.152946, 0.159012, 0.165073, 0.171128, 0.177176, 0.183217, 0.189251, 0.195279,
                        0.201299, 0.207311, 0.213316, 0.219312, 0.225300, 0.231280, 0.237251, 0.243213, 0.249166, 0.255110, 0.261043, 0.266967, 0.272881, 0.278785, 0.284678, 0.290561,
                        0.296432, 0.302292, 0.308141, 0.313978, 0.319804, 0.325617, 0.331418, 0.337206, 0.342982, 0.348745, 0.354495, 0.360231, 0.365954, 0.371663, 0.377358, 0.383039,
                        0.388705, 0.394356, 0.399993, 0.405615, 0.411221, 0.416812, 0.422387, 0.427946, 0.433489, 0.439016, 0.444526, 0.450019, 0.455495, 0.460954, 0.466396, 0.471820,
                        0.477227, 0.482615, 0.487985, 0.493337, 0.498670, 0.503985, 0.509280, 0.514556, 0.519813, 0.525050, 0.530267, 0.535464, 0.540641, 0.545798, 0.550934, 0.556050,
                        0.561144, 0.566217, 0.571269, 0.576299, 0.581308, 0.586294, 0.591259, 0.596201, 0.601121, 0.606018, 0.610892, 0.615743, 0.620571, 0.625375, 0.630156, 0.634913,
                        0.639646, 0.644355, 0.649040, 0.653700, 0.658336, 0.662947, 0.667532, 0.672093, 0.676628, 0.681138, 0.685622, 0.690080, 0.694512, 0.698918, 0.703297, 0.707650,
                        0.711977, 0.716276, 0.720548, 0.724794, 0.729012, 0.733202, 0.737365, 0.741500, 0.745607, 0.749685, 0.753736, 0.757758, 0.761751, 0.765716, 0.769652, 0.773559,
                        0.777437, 0.781285, 0.785104, 0.788893, 0.792653, 0.796382, 0.800082, 0.803751, 0.807390, 0.810999, 0.814577, 0.818124, 0.821641, 0.825126, 0.828580, 0.832003,
                        0.835395, 0.838755, 0.842084, 0.845380, 0.848645, 0.851878, 0.855079, 0.858247, 0.861383, 0.864487, 0.867558, 0.870596, 0.873601, 0.876574, 0.879513, 0.882419,
                        0.885292, 0.888132, 0.890938, 0.893710, 0.896449, 0.899154, 0.901825, 0.904462, 0.907064, 0.909633, 0.912167, 0.914667, 0.917133, 0.919563, 0.921959, 0.924321,
                        0.926647, 0.928939, 0.931195, 0.933416, 0.935602, 0.937753, 0.939869, 0.941949, 0.943993, 0.946002, 0.947975, 0.949912, 0.951814, 0.953680, 0.955509, 0.957303,
                        0.959060, 0.960782, 0.962467, 0.964116, 0.965728, 0.967304, 0.968843, 0.970346, 0.971813, 0.973242, 0.974635, 0.975992, 0.977311, 0.978593, 0.979839, 0.981048,
                        0.982219, 0.983354, 0.984451, 0.985512, 0.986535, 0.987521, 0.988469, 0.989381, 0.990255, 0.991092, 0.991891, 0.992653, 0.993377, 0.994064, 0.994714, 0.995326,
                        0.995900, 0.996437, 0.996937, 0.997398, 0.997822, 0.998209, 0.998557, 0.998869, 0.999142, 0.999378, 0.999576, 0.999736, 0.999859, 0.999943, 0.999991, 1.000000,
                        0.999972, 0.999906, 0.999802, 0.999661, 0.999481, 0.999264, 0.999010, 0.998718, 0.998388, 0.998020, 0.997615, 0.997172, 0.996692, 0.996174, 0.995618, 0.995025,
                        0.994394, 0.993726, 0.993020, 0.992277, 0.991496, 0.990678, 0.989823, 0.988930, 0.988000, 0.987032, 0.986028, 0.984986, 0.983907, 0.982791, 0.981638, 0.980448,
                        0.979221, 0.977957, 0.976656, 0.975318, 0.973943, 0.972532, 0.971084, 0.969599, 0.968078, 0.966521, 0.964926, 0.963296, 0.961629, 0.959926, 0.958186, 0.956411,
                        0.954599, 0.952751, 0.950868, 0.948948, 0.946993, 0.945002, 0.942975, 0.940913, 0.938815, 0.936682, 0.934514, 0.932310, 0.930071, 0.927797, 0.925488, 0.923144,
                        0.920766, 0.918352, 0.915904, 0.913422, 0.910905, 0.908353, 0.905767, 0.903147, 0.900494, 0.897806, 0.895084, 0.892328, 0.889539, 0.886716, 0.883860, 0.880970,
                        0.878048, 0.875092, 0.872103, 0.869081, 0.866026, 0.862939, 0.859819, 0.856667, 0.853482, 0.850266, 0.847017, 0.843736, 0.840423, 0.837079, 0.833703, 0.830296,
                        0.826857, 0.823387, 0.819886, 0.816354, 0.812792, 0.809198, 0.805575, 0.801920, 0.798236, 0.794521, 0.790777, 0.787002, 0.783198, 0.779365, 0.775502, 0.771609,
                        0.767688, 0.763737, 0.759758, 0.755750, 0.751714, 0.747649, 0.743557, 0.739436, 0.735287, 0.731110, 0.726906, 0.722674, 0.718416, 0.714130, 0.709817, 0.705477,
                        0.701111, 0.696718, 0.692299, 0.687854, 0.683383, 0.678886, 0.674364, 0.669816, 0.665243, 0.660644, 0.656021, 0.651373, 0.646701, 0.642004, 0.637283, 0.632538,
                        0.627769, 0.622976, 0.618160, 0.613320, 0.608458, 0.603572, 0.598664, 0.593733, 0.588779, 0.583804, 0.578806, 0.573787, 0.568746, 0.563683, 0.558599, 0.553495,
                        0.548369, 0.543222, 0.538055, 0.532868, 0.527661, 0.522434, 0.517187, 0.511920, 0.506635, 0.501330, 0.496006, 0.490664, 0.485303, 0.479923, 0.474526, 0.469111,
                        0.463678, 0.458227, 0.452759, 0.447274, 0.441773, 0.436254, 0.430719, 0.425168, 0.419601, 0.414018, 0.408420, 0.402806, 0.397177, 0.391532, 0.385873, 0.380200,
                        0.374512, 0.368810, 0.363094, 0.357365, 0.351622, 0.345865, 0.340096, 0.334314, 0.328519, 0.322712, 0.316892, 0.311061, 0.305218, 0.299363, 0.293498, 0.287621,
                        0.281733, 0.275834, 0.269926, 0.264007, 0.258078, 0.252139, 0.246191, 0.240233, 0.234267, 0.228291, 0.222307, 0.216315, 0.210314, 0.204306, 0.198290, 0.192266,
                        0.186235, 0.180197, 0.174152, 0.168101, 0.162043, 0.155980, 0.149910, 0.143835, 0.137754, 0.131668, 0.125577, 0.119481, 0.113381, 0.107277, 0.101168, 0.095056,
                        0.088940, 0.082821, 0.076699, 0.070573, 0.064446, 0.058315, 0.052183, 0.046048, 0.039912, 0.033774, 0.027635, 0.021495, 0.015354, 0.009213, 0.003071, -0.003071,
                        -0.009213, -0.015354, -0.021495, -0.027635, -0.033774, -0.039912, -0.046048, -0.052183, -0.058315, -0.064446, -0.070573, -0.076699, -0.082821, -0.088940, -0.095056, -0.101168,
                        -0.107277, -0.113381, -0.119481, -0.125577, -0.131668, -0.137754, -0.143835, -0.149910, -0.155980, -0.162043, -0.168101, -0.174152, -0.180197, -0.186235, -0.192266, -0.198290,
                        -0.204306, -0.210314, -0.216315, -0.222307, -0.228291, -0.234267, -0.240233, -0.246191, -0.252139, -0.258078, -0.264007, -0.269926, -0.275834, -0.281733, -0.287621, -0.293498,
                        -0.299363, -0.305218, -0.311061, -0.316892, -0.322712, -0.328519, -0.334314, -0.340096, -0.345865, -0.351622, -0.357365, -0.363094, -0.368810, -0.374512, -0.380200, -0.385873,
                        -0.391532, -0.397177, -0.402806, -0.408420, -0.414018, -0.419601, -0.425168, -0.430719, -0.436254, -0.441773, -0.447274, -0.452759, -0.458227, -0.463678, -0.469111, -0.474526,
                        -0.479923, -0.485303, -0.490664, -0.496006, -0.501330, -0.506635, -0.511920, -0.517187, -0.522434, -0.527661, -0.532868, -0.538055, -0.543222, -0.548369, -0.553495, -0.558599,
                        -0.563683, -0.568746, -0.573787, -0.578806, -0.583804, -0.588779, -0.593733, -0.598664, -0.603572, -0.608458, -0.613320, -0.618160, -0.622976, -0.627769, -0.632538, -0.637283,
                        -0.642004, -0.646701, -0.651373, -0.656021, -0.660644, -0.665243, -0.669816, -0.674364, -0.678886, -0.683383, -0.687854, -0.692299, -0.696718, -0.701111, -0.705477, -0.709817,
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

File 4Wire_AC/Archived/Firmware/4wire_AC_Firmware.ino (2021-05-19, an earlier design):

/*
    This code is for a 4-wire AC voltage divider circuit card in taking temperature measurements with Lakeshore millikelvin thermometers.
    Intended for a Teensy 3.2
    Code written by Stephen Shaw 10 July 2020
    Winona Astrophysics Group 2020, H.aHK Box project
    Version: 1.0
*/

/*
   Device Definition
   dev1 : 24-bit ADC
   dev2 : Potentiometer 1 (1M) on channel 1
   dev3 : Potentiometer 2 (1M) on channel 2
   dev4 : Potentiometer 3 (1M) on channel 3
   dev5 : potentiometer 4 (1M) on channel 4
   dev6 : 24-bit ADC 2 (I2C Wire1)
*/

#include <Adafruit_NAU7802.h> // Library for using the ADC
#include <Wire.h> // Library for using simple I2C commands for the digi potentiometer
#include <SPI.h>

String card_id = "4-wire AC 1"; // specify card identity for returning to RPI in startup
#define card_address 2 // address for I2C comm with RPI
Adafruit_NAU7802 nau; // define sensor for NAU7802 library

byte dev1_address = 42; //0101010
byte dev2_address = 44; //0101100, first 5 bits set, last two defined as AD0 adn AD1 values
byte dev3_address = 45; //0101101, first 5 bits set, last two defined as AD0 adn AD1 values
byte dev4_address = 46; //0101110, first 5 bits set, last two defined as AD0 adn AD1 values
byte dev5_address = 47; //0101111, first 5 bits set, last two defined as AD0 adn AD1 values
byte dev6_address = 42; //0101010

byte AD0_1_pin = 0; //define digital write pins for I2C interfacing with potentiometers, programable addresses
byte AD1_1_pin = 1;
byte AD0_2_pin = 2;
byte AD1_2_pin = 3;
byte AD0_3_pin = 7;
byte AD1_3_pin = 8;
byte AD0_4_pin = 9;
byte AD1_4_pin = 11;
byte ADC_ready_1_pin = 4; // define byte data channel for ADC 1 to say when a new reading is available
byte ADC_ready_2_pin = 5; // define byte data channel for ADC 2 to say when a new reading is available
byte reset_pin = 6; //connect channel to reset analog in pin, flipped HIGH if card is shut down or reset from RPI
byte output_pin = 9;
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

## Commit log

2019-06-06 initial folder setup and some file moving
    [Backplane.SLDPRT, Display.SLDPRT, Eurocard.SLDPRT, Fan.SLDPRT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]
2019-06-06 folder structure
    [PCN13-64S-2.54DS.stp]
2019-07-02 card footprints
    [BackPlane #1.DXF, Expansion Card.DXF]
2019-07-11 WIP BOM
    [BomWIP.ods, BomWIP.xls]
2019-07-11 updated bom
    [BomWIP.ods, BomWIP.xls]
2019-07-11 bom update
    [BomWIP.ods, BomWIP.xls]
2019-07-11 bom update?
    [BomWIP.ods, BomWIP.xls]
2019-07-11 bom update post meeting
    [BomWIP.ods, BomWIP.xls]
2019-07-23 technical guide update?
    [BomWIP.ods, BomWIP.xls]
2019-07-24 socket test files
    [BOM_PartType-HaHK_Box.xls, PCard.step, Pick Place for PCard.csv]
2019-07-24 technical guide work
    [PCN13-64S-2.54DS.stp]
2019-07-24 socket test
    [PCB1.step]
2019-07-25 socket test printable
    [PCB1.step]
2019-08-05 powerpoint with pics
    [BOM_PartType-HaHK_Box.xls, PCardWBJ.step, Pick Place for PCardWBJ.csv]
2019-08-05 presentation work, new renders
    [BOM_PartType-HaHK_Box.xls, PCardWBJ.step, Pick Place for PCardWBJ.csv]
2019-08-23 just checking
    [BomWIP.ods, BomWIP.xls]
2019-11-05 vectorized logos
    [hardware.astronomy.dxf, wLogoFlameSide.dxf, wLogoFlameTop.dxf]
2019-11-07 p-card work and bom
    [BOM.ods]
2019-12-18 backplane schematic pdf
    [BOM_PartType-HaHK_Box.xls]
2020-05-30 checkpoint reorganization and report
    [BOM.ods, BOM_PartType-HaHK_Box.xls, BomWIP.ods, BomWIP.xls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]
2020-05-31 report not proof-read and p-card officalized
    [BOM.ods, BOM_PartType-HaHK_Box.xls, Expansion Card.DXF, PCB1.step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]
2020-06-03 circuit maker output
2020-06-05 Circuit Photos and Researcher Guide Update
2020-06-11 Logistics folder
    [cpsaat11.xlsx, graphedData.xlsx]
2020-08-09 long long overdue commit
    [2020-07-09T105658.csv, 2020-07-09T122409.csv, 2020-07-09T122409.xlsx, BOM_PartType-HaHK_Box.xls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]
2020-11-30 presentations and outputs
    [BOM_PartType-HaHK_Box.xls, Backplane_keepOut9-2020.DXF, PCardWBJ.step, layers.ods]
2021-03-25 backplane output
    [BOM_PartType-HaHK_Box.xls, HaHK_Box.PrjPcb, PCard.SchDoc, PCardWBJ.step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]
2021-11-13 Delete 4WireACBridge directory
    Restructuring Directory to contain all these old things AND new firmware to be worked on
    [2V_NAU7802_output_9_16_20.xlsx, 300mV_NAU7802_output_9_16_20.xlsx, 4ch GRT reader.PcbDoc, 4ch GRT reader.PrjPCB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]
2021-12-03 Create HahkBoxBackUpFile.py
    back up file just in case SD card is missing again
2022-02-01 Update RMSreadInNAU_firmWareV1_17Nov2021.ino
    Added comments, revised code to allow for different frequency inputs besides 1 Hz.
2022-02-09 Update RMSreadInNAU_firmWareV1_17Nov2021.ino
    Changed from function sine wave generation to table defined sine wave generation for output to teensy DAC. Added Read Out Rate user definition functionality. Refined frequency definition functionalit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
2022-03-02 Adding newest 4 wire firmware
    Newest firmware file for 4 wire AC measurement card includes usage of 16 bit ADC (ADS1115) and further refinement of delay between measurements.
2022-03-02 Adding lab 5 files
    Adding files with data from firmware output and csv's with the sine wave table values used in the firmware for driving the DAC sine wave output.
    [ADC_Investigation_Data.xlsx, Freq_and_NumCyc_testing_.xlsx, Mean&STD_vs_Frequency.xlsx, Mean&STD_vs_NumCycles.xlsx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]
2022-06-14 arduino file for testing raspberry pi API
    a couple bugs to fix:
    randomized values not being added and sent
    speed of communication
2022-06-14 up to date h.ahk box API
    the boot function works properly with one follower device connected to it
    currently spending time on the poll function. so far it almost complete, it should work as it is now but still debugging a few issues with the Arduino.
    - need to clean up past comments and unused commented out code
    - fix communication timing error
    - resolve value issues with arduino communication
    - change boot function
2022-06-22 "some what" finalized version of arduino test code
    this version has shown to work as intended. it can randomly decide to send data and decide when to not send data. it can send random values and random number of bytes
    the only thing left is to test that it can communicate when there are other i2c devices connected on the same line.
2022-06-27 Current h.ahkBox
    I plan on doing some larger changes to it so I added it's previous version here in case i broke it beyond a quick repair.
    The next update if all goes well will be will the tabs being able to reload ned graph variables.
2022-07-01 created Card Library python module
    we may not need an entirely separate module for handing card information and formatting but currently it might be a good idea as to keep things a bit more organized and less confusing and cluttered. 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
    note: (may or may not be needed) we may also need to have a seprate file that has the raw byte information saved as well so that incase there is weird error we can see bit by bit whe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
2022-07-18 Sidebar implentation
    I think i will use this rather than the tabs
    there are a few issues currently with as the side bar is only a small square box in the upper left hand corner instead of exending to the bottom of the page and it overlaps the apge when i want every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
    I think the way this component is formatted, it will be easier to implement pages and to toggle them on off as cards are available and not available- (I think I don't know yet)
    any errors stated as tab errors can easily be ignored as they are not relevant in this version.
2022-07-19 Pseudo code for card library
    currently still trying to figure how I want data to be send
    right now i have is so there will be a separate function that will interpret what card it is and the from there it will go to a specific card function and based on the logistical header it will then 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
2022-08-04 new daily files
    made it so that the library will create a new file everyday. this current way was based off the easiest way I could think of. it will simply name itself the day month and year and when the day change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
2022-08-12 added card type function
    I added a new function that can be used to see what card type is sending data and from there using if statements and the perform that specific card function
    currently the it does not work for some reason? I am not sure exactly why?
    I keep getting this error TypeError: 'NoneType' object is not subscriptable
    also note: change if statements to elif instead of just if
2022-08-12 updated for current version of card Library
2022-08-12 testing just the h.ahk version
    this is for testing the h.ahk version. if you want to test out the card library you will need to make sure the arduino is sending very specific values and values sizes other wise the results will not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
    as an example for what the arduino can send if you want to test it:
    (0x33, 0x88, 0x01, 0x02, 0xa3, 0x04, 0x05,)
    add this to data portion fo the arduino code instead of the function that creates adn random array size and random values in that arrary.
